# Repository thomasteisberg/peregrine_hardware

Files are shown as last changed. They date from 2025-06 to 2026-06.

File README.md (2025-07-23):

# Peregrine Hardware Files

This repository contains hardware design and fabrication files for the Peregrine UAV-borne radio echo sounder (Part of the ORCA project)

See https://orca.radioglaciology.com/docs/peregrine/ for details

Design files produced by us are available under an [MIT License](LICENSE). For vendor CAD, please check with individual vendors.

## Payload Enclosure

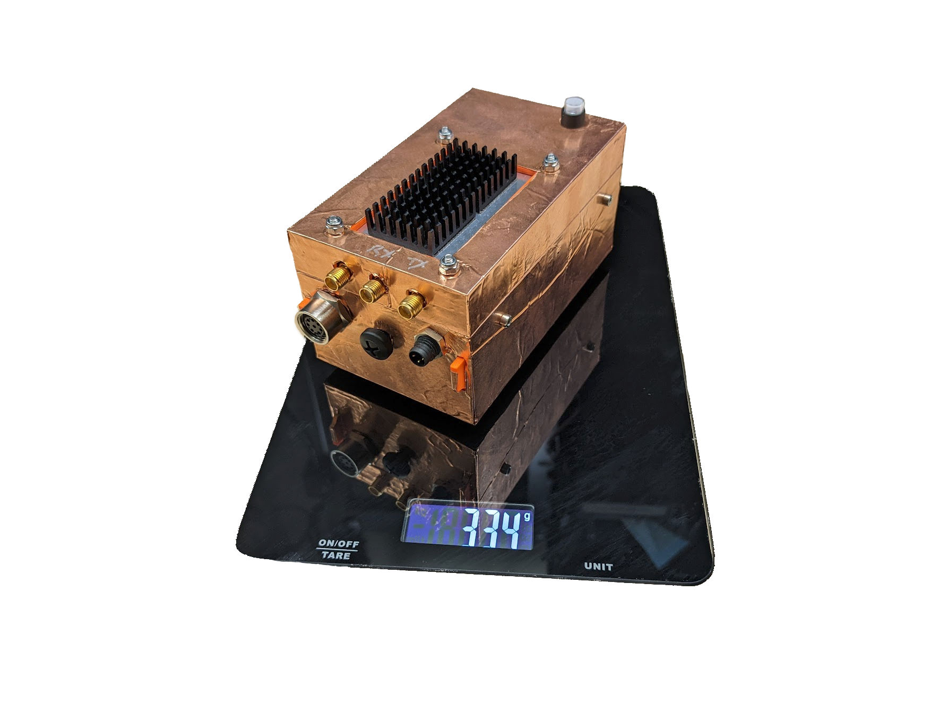
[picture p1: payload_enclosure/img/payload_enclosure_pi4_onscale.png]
Photo of an assembled payload enclosure


The [payload enclosure](payload_enclosure/) is the box containing the Ettus b205-mini SDR and the Raspberry Pi for the Peregrine UAS.

This assembly normally lives in the nosecone of the Peregrine UAV, as seen in the photo below, however it can be re-purpose in other ways.

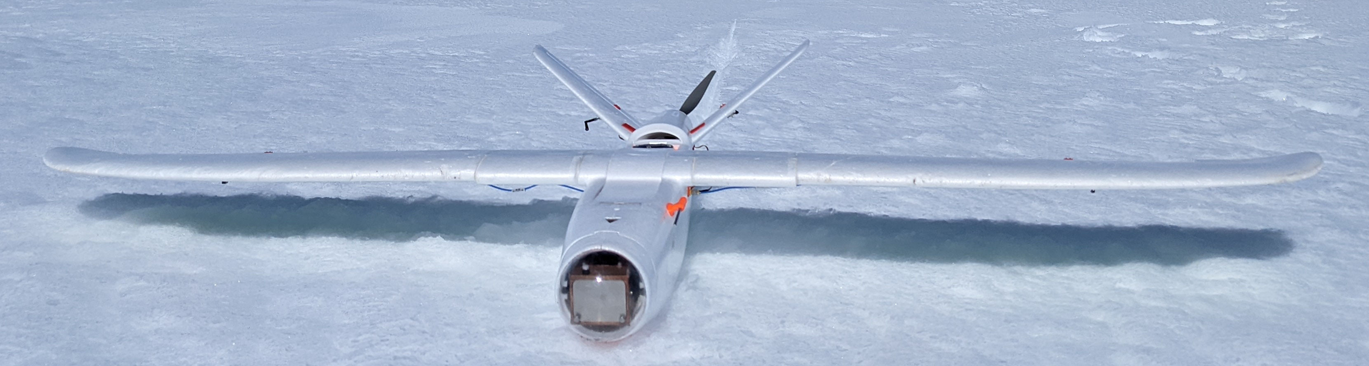
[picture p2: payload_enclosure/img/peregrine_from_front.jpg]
Front view of the Peregrine UAS showing the payload enclousure within the nosecone


## Payload enclosure PCBs

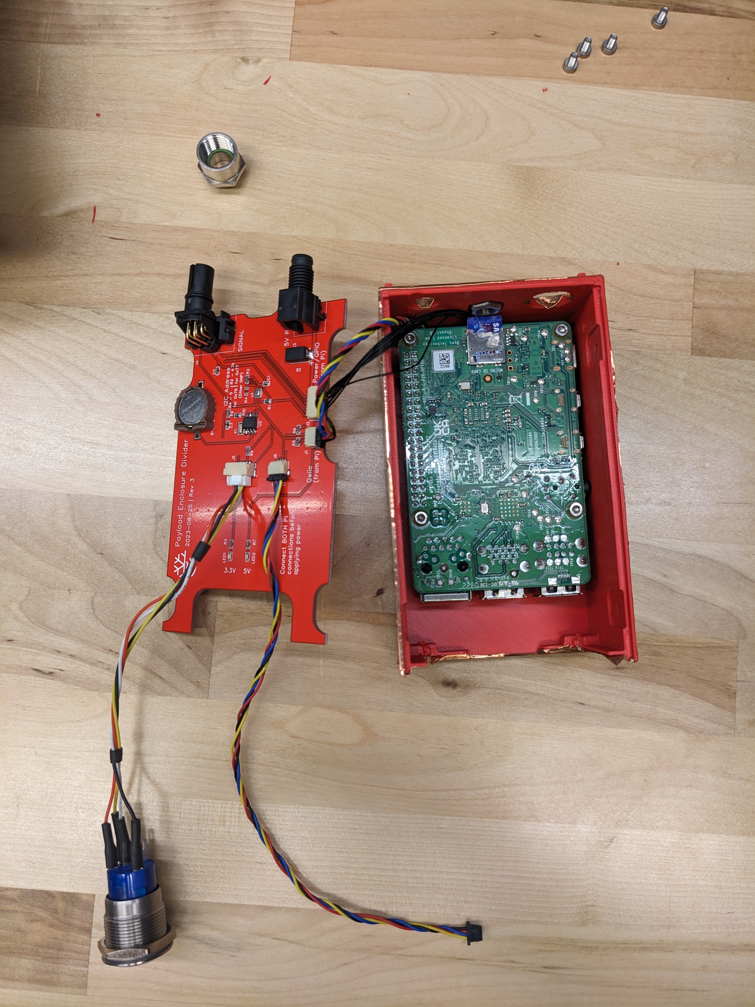
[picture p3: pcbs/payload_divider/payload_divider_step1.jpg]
Peregrine Payload Divider PCB


There are two custom PCBs that live inside the payload enclosure. They are:

* [Peregrine Pi Hat](pcbs/pi_hat/)
* [Peregrine Payload Divider](pcbs/payload_divider/)

## Other PCBs

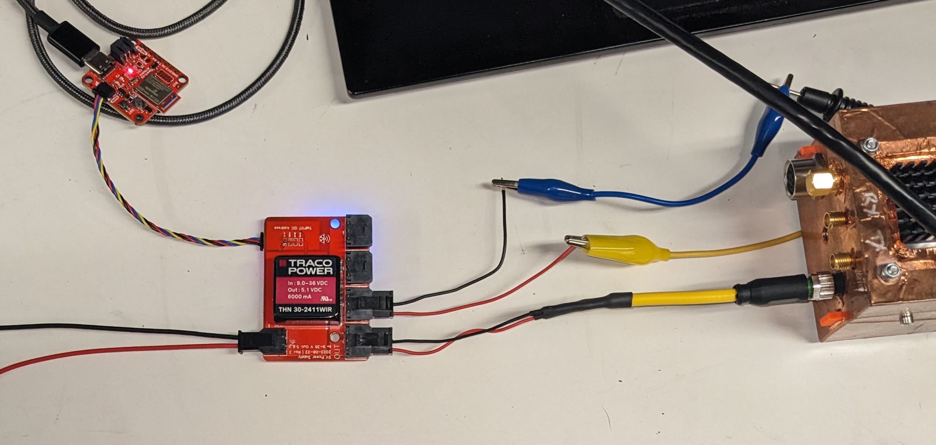
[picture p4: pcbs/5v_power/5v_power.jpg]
5V switching regulator PCBA


* [5V Switching Power Supply](pcbs/5v_power/)

## Antennas

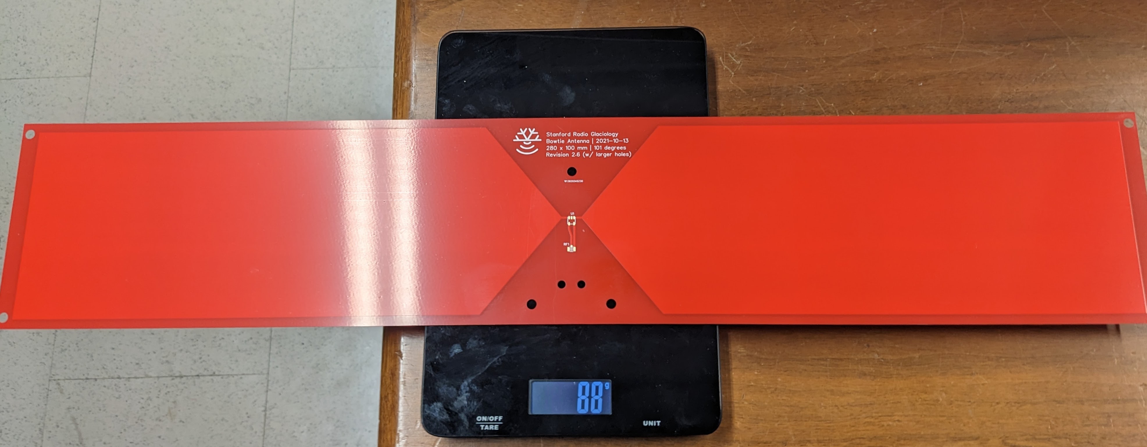
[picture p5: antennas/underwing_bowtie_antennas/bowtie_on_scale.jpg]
Bowtie antenna on a scale


* [Peregrine under-wing edge-cut bowtie antennas](antennas/underwing_bowtie_antennas/)

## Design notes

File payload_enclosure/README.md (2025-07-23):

# Peregrine Payload Enclosure

This is the main radar payload enclosure for Peregrine.

See https://orca.radioglaciology.com/docs/peregrine/payload/ for details.

The `design_files` directory has STEP assembly files and Autodesk Inventor
[Pack and Go files](https://help.autodesk.com/view/INVNTOR/2025/ENU/?guid=GUID-730304AA-13BD-467B-9351-C7C1362876BD)
fpr each of the variants described below.

The `fabrication_files_(variant)` contain ready-to-use files for fabrication. See [fabrication notes](#fabrication) below.

### Payload enclosure PCBs

There are also two custom PCBs that live inside the payload enclosure. They are:

* [Peregrine Pi Hat](../pcbs/pi_hat/)
* [Peregrine Payload Divider](../pcbs/payload_divider/)

## Variants

There are three variants included here:

### Pi 5

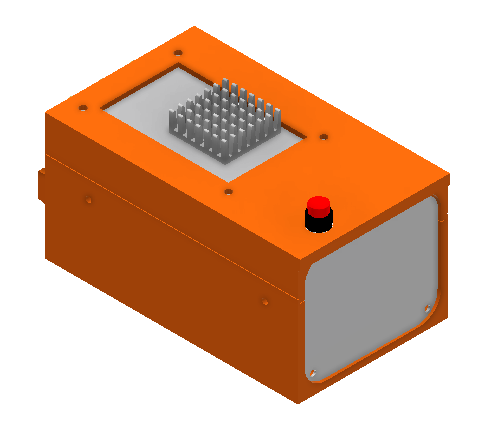
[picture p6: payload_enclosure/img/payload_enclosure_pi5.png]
Payload enclousure with Pi 5 CAD rendering


This version fits in the Peregrine nosecone and contains a Raspberry Pi 5.

This version is identical to the Pi 4 version except for an different heatsink design.

### Pi 5 with NVMe SSD

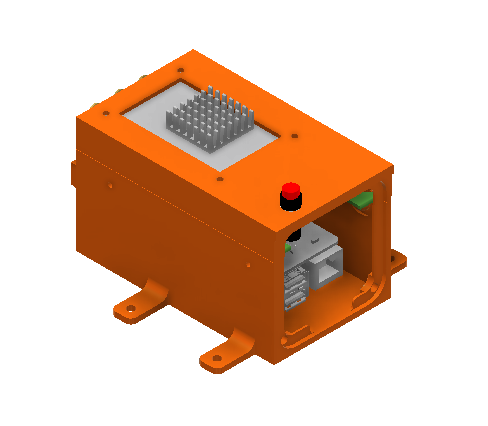
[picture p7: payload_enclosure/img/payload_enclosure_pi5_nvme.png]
Extended height payload enclosure with Pi 5 and an NVMe SSD


This is a variant of the above with the Pi-side of the shell vertically extended to make space for an NVMe SSD. See https://orca.radioglaciology.com/docs/peregrine/payload/data-storage/ for more information.

Note that because this is a vertically stretch version, it does not fit in the Peregrine nosecone without modification. This variant was designed for other uses and also has 4 mounting holes added on small tabs.

### Pi 4 (archived)

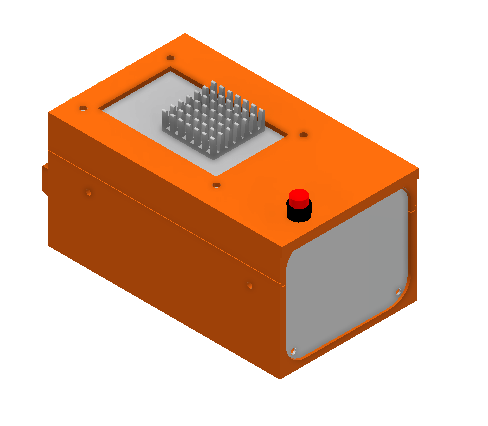
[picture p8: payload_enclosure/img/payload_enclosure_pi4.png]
Payload enclosure with Pi 4 CAD rendering


This version fits in the Peregrine nosecone and contains a Raspberry Pi 4.

For new builds, using the Raspberry Pi 5 is strongly recommended.

## Fabrication notes

### 3D Printing

The following components are intended to be 3D printed:

* `pi_shell.stl`
* `sdr_shell.stl`

They are designed for printing on an FDM printer. They should be printed in ASA
or a similar material (not PLA) to avoid warping due to the heat from the components
inside.

### Laser Cutting

The `cover_plate_2holes_standardfit_0p5mm_tolerance.dxf` file is intended for
laser cutting. Our default option is to cut this out of 1 mm (0.040") aluminum.
(We use SendCutSend's 5052 H32 Aluminum cutting service.)

For the Peregrine UAS, it can be useful to use this plate as a fine-tuning
adjustment for the center of gravity, since it sits in the very front of the
aircraft. For this purpose, our flight kit usually contains copies of this part
cut out of the following materials (all from SendCutSend):

* 1 mm 5052 Aluminum
* 1 mm Copper
* 1.5 mm Copper

This provides enough mass variation to be able to fine-tune the center of gravity
as needed.
(The adjustable battery tray provides the main center of gravity adjustment.
This is for minor fine-tuning only.)

### CNC Machining

The `pi(4/5)_heat_block.stp` and associated `pi(4/5)_heat_block.pdf` files are
intended for CNC machining. The PDF file is a drawing that specifies the thread
tapping needed for the mounting holes.

We get this fabricated out of aluminum. We have used several CNC vendors with
good results every time.

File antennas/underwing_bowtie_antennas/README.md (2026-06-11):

# Peregrine Underwing Edge-Cut Bowtie Antenna

Bowtie antenna on a scale

This is the design for the edge-cut bowtie radar antennas mounted under the Peregrine wings.

The `.zip` file is an export from EasyEDA. It can be uploaded to EasyEDA as a new project. It is also possible to load in KiCAD using the EasyEDA importer (File > Import Non-KiCad Project ... > EasyEDA (JLCEDA) Std Backup).

The source project in EasyEDA is titled `bowtie-v2.6-with-larger-holes`.

## Production notes

This antenna is designed to be printed on standard FR4. FR4 is generally not controlled for dielectric permittivity, so results may vary and each individual unit should be checked for S11 before use.

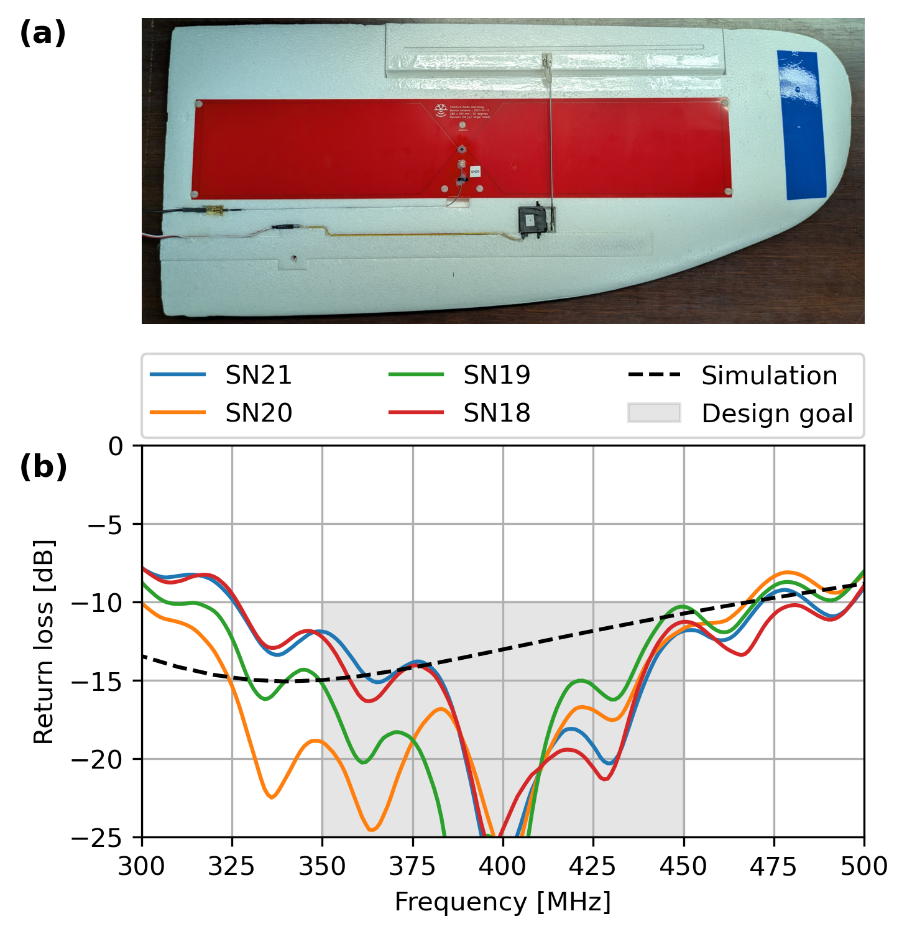
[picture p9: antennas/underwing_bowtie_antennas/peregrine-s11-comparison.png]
Antenna S11 results from several individual units


The design is not particularly sensitive to the FR4 thickness. For Peregrine, I had this produced on 0.6 mm FR4 substrate, which significantly reduces the weight. Note that 0.6mm FR4 substrate is not rigid on its own, which may be a downside depending on how you plan to use this.

The total width (588 mm) is larger than what many PCB manufacturers can do. We produced this PCB with PCBWay.

If you want to copy our settings exaclty, the design is shared on PCBWay: https://www.pcbway.com/project/shareproject/Peregrine_under_wing_bowtie_antenna_c198dc1e.html

## Bill of Materials

* U1 (balun): [Mini-Circuits TC4-1W+](https://www.minicircuits.com/WebStore/dashboard.html?model=TC4-1W%2B)
* RF1 (U.FL connector): [U.FL-R-SMT-1(40)](https://www.mouser.com/ProductDetail/Hirose-Connector/U.FL-R-SMT-140?qs=PABxe4V6HDrVNWAmh6WKgw%3D%3D&srsltid=AfmBOopH3k4K2ASrjq8ZP3SyGSTScw2wuCMmbPjLw4Hym1gIAsaXcrwh)
* Suggested U.FL to SMA cable: [CSI-SGFI-100-UFFR ](https://www.mouser.com/ProductDetail/TE-Connectivity-Linx-Technologies/CSI-SGFI-100-UFFR?qs=j%252B1pi9TdxUbVF8XdLr3HSg%3D%3D)
* Silicone adhesive: [EGS10C-20G](https://www.digikey.com/en/products/detail/chip-quik-inc/EGS10C-20G/10059587)

## Design notes

The design is loosely described in our first Peregrine paper: [Development of a UAV-Borne Pulsed Ice-Penetrating Radar System](https://doi.org/10.1109/IGARSS46834.2022.9883583) [[PDF]](https://www.thomasteisberg.com/assets/pdf/igarss2022_peregrine.pdf)

The design was inspried by this paper: [A 900MHz shielded bow-tie antenna system for ground penetrating radar](https://doi.org/10.1109/ICGPR.2010.5550125)

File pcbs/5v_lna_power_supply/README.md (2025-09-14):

# 5V LNA Power Supply

**This PCBA is NOT a core Peregrine component. It is part of the "Peregrine+" ground-based system. It may be useful for various customized setups. It should not be used for high current applications such as UAV motors.**

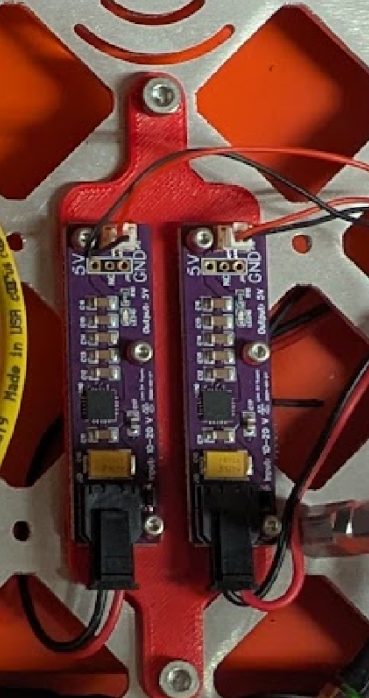
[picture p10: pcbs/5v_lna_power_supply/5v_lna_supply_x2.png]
Two 5V LNA power supplies in the SORA configuration


This project contains two simple designs for relatively low noise 5V power supplies intended to be used for powering low noise amplifiers. One is intended to be paired with a switching power supply providing slightly over 5V (such as the switching 5V supply in this repo configured to provide 5.2 or 5.3V). The other is a fully linear path from 10-20V input directly. The version we've used more extensively is the one that goes directly from the 10-20V version.

The `.zip` file is an export from EasyEDA. It can be uploaded to EasyEDA as a new project. It is also possible to load in KiCAD using the EasyEDA importer (File > Import Non-KiCad Project ... > EasyEDA (JLCEDA) Std Backup).

The source project in EasyEDA is titled `5v-lna-supply`.

## Fabrication notes

The Gerber files, BOM, and Pick and Place files are in the [fabrication_files](fabrication_files/) subdirectory. I've produced this PCB with JLCPCB in the past, but there's nothing particularly unique about the requirements. Any board house should be able to do it.

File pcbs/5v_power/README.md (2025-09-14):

# 5V Power for Peregine Payload

5V power PCB hooked up to a power supply, the radar payload, an a data logger

This is a simple PCB that hosts a high-quality switching 5V regulator from Traco: [THN 30-2411WIR](https://www.tracopower.com/model/thn-30-2411wir) (Note that this is a fairly expensive part -- about $80 in small quantity.)

This is used as the primary 5V power supply for the Peregrine UAV, powering both the radar and the rest of the UAV electronics. (It does not live inside the payload enclosure.)

There are detailed instructions for making the appropriate power harnessing on the main orca website: [5V Power Board and Power Harnesses](https://orca.radioglaciology.com/docs/peregrine/power/)

In addition to power regulation, the board has voltage, current, and temperature sensing, all available on an I2C bus with two [Qwiic](https://www.sparkfun.com/qwiic)-compatible connectors (for daisy-chaining). In the photo above, it is shown connected to a [SparkFun OpenLog Artemis](https://www.sparkfun.com/sparkfun-openlog-artemis.html) for bench logging of the sensor data. The I2C connection can also be connected to the data port on the radar payload and logged on the Pi using the [uav_radar_logger](https://github.com/thomasteisberg/uav_radar_logger) service.

The `.zip` file is an export from EasyEDA. It can be uploaded to EasyEDA as a new project. It is also possible to load in KiCAD using the EasyEDA importer (File > Import Non-KiCad Project ... > EasyEDA (JLCEDA) Std Backup).

The source project in EasyEDA is titled `uav-5v-supply-v4`.

**Note that this is NOT the version used on the Penguin UAV. That version has the same circuity but a different physical form factor.**

## Fabrication notes

The Gerber files, BOM, and Pick and Place files are in the [fabrication_files](fabrication_files/) subdirectory. I've produced this PCB with JLCPCB in the past, but there's nothing particularly unique about the requirements. Any board house should be able to do it.

For part availability and process reasons, I have never had any of the through-hole parts assembled by JLCPCB, however it should be fine to do so if your PCBA manufacturer has the parts in stock. The inductor (`L1`, TCK-141) is often not available in PCBA manufacturer part catalogs, so you may need to source and assemble that part separately.

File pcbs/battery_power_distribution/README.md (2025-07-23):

# Battery Power Distribution

**This PCBA is NOT a core Peregrine component. It is part of the "Peregrine+" ground-based system. It may be useful for various customized setups. It should not be used for high current applications such as UAV motors.**

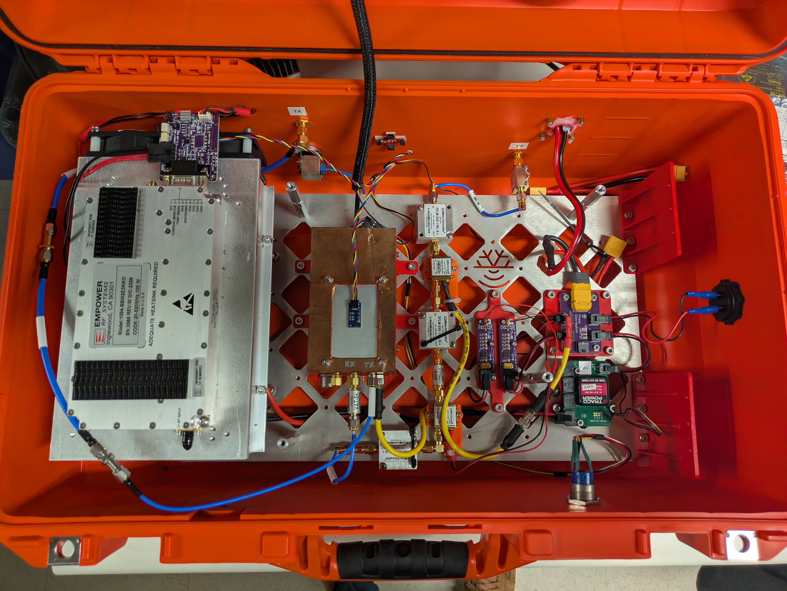
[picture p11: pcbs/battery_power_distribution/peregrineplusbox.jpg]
The Peregrine+ box, with the power distribution PCB visible on the right side


This is a very simple convenience PCB that connects an XT60 connector to 5 Molex Micro-Fit 3 2-pin connectors. It is used to cleanly wire up battery power to several components.

The `.zip` file is an export from EasyEDA. It can be uploaded to EasyEDA as a new project. It is also possible to load in KiCAD using the EasyEDA importer (File > Import Non-KiCad Project ... > EasyEDA (JLCEDA) Std Backup).

The source project in EasyEDA is titled `batt-power-distribution`.

## Fabrication notes

The Gerber files, BOM, and Pick and Place files are in the [fabrication_files](fabrication_files/) subdirectory. I've produced this PCB with JLCPCB in the past, but there's nothing particularly unique about the requirements. Any board house should be able to do it.

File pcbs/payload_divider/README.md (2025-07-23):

# Peregrine Payload Divider

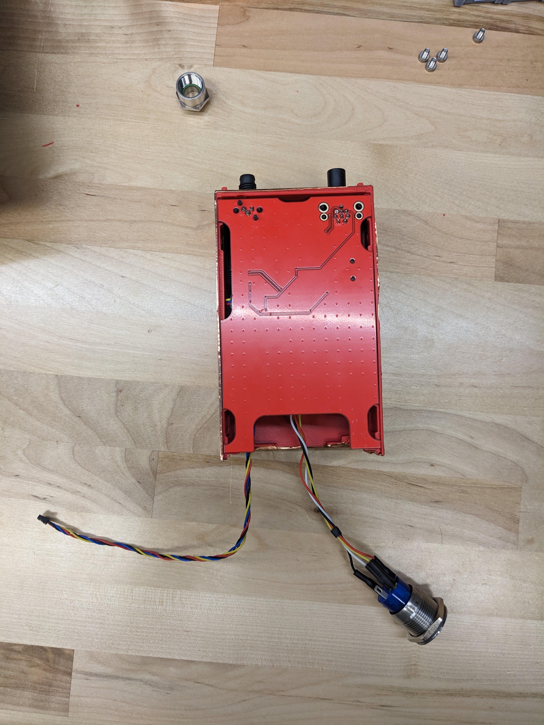
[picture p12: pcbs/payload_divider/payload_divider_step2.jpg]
Bottom side of the payload divider PCB after being placed in the payload enclosure
Payload divider PCB before being flipped into case 

The payload "divider" PCB divides the Raspberry Pi half of the shell from the SDR half of the shell. The PCB physically sits in the middle of the two clamshell pieces, hence its name.

This PCB serves as an external interface to the Pi as well as directly hosting a real-time clock and a temperature sensor. The external connectors to the payload enclosure live on this PCB.

The `.zip` file is an export from EasyEDA. It can be uploaded to EasyEDA as a new project. It is also possible to load in KiCAD using the EasyEDA importer (File > Import Non-KiCad Project ... > EasyEDA (JLCEDA) Std Backup).

The source project in EasyEDA is titled `payload-divider-v4`.

## Fabrication notes

The Gerber files, BOM, and Pick and Place files are in the [fabrication_files](fabrication_files/) subdirectory. I've produced this PCB with JLCPCB in the past, but there's nothing particularly unique about the requirements. Any board house should be able to do it.

For part availability and process reasons, I have never had any of the through-hole parts assembled by JLCPCB, however it should be fine to do so if your PCBA manufacturer has the parts in stock.

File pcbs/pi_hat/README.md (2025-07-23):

# Peregrine Pi Hat

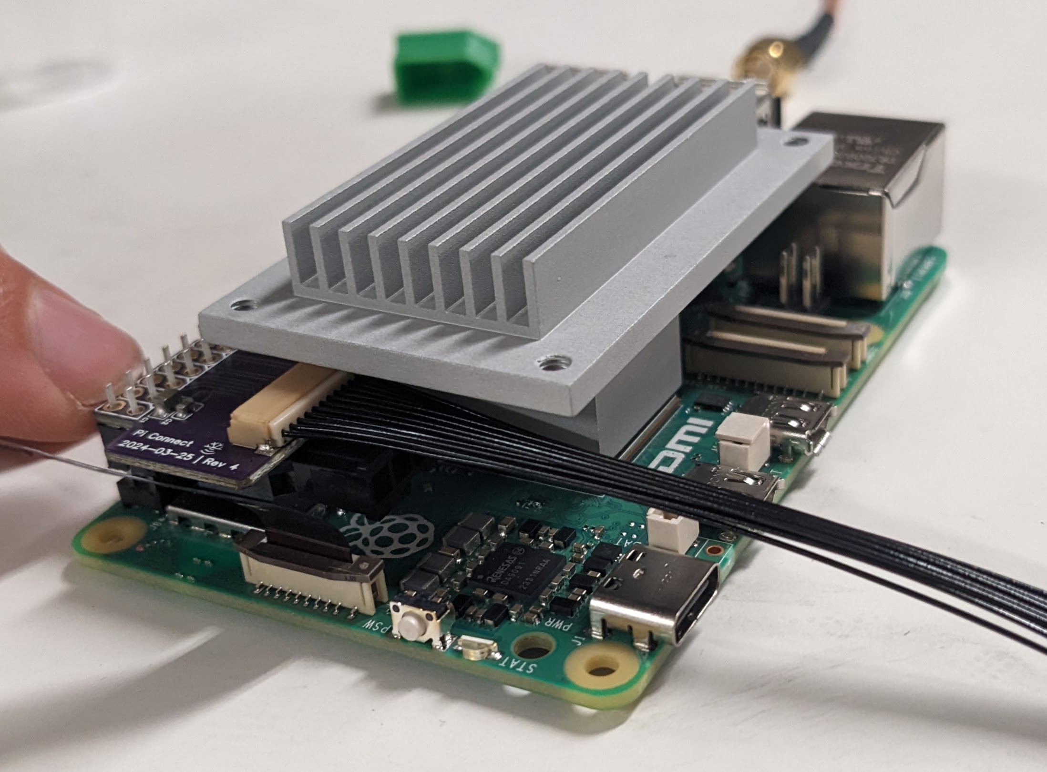
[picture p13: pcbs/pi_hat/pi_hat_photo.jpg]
Pi Hat installed on a Pi 5 under heatsink


This is a very small PCB whose only function is to interface with the power and I2C connections on the Pi's GPIO header. It's the purple board on the left of the photo above.

The `.zip` file is an export from EasyEDA. It can be uploaded to EasyEDA as a new project. It is also possible to load in KiCAD using the EasyEDA importer (File > Import Non-KiCad Project ... > EasyEDA (JLCEDA) Std Backup).

The source project in EasyEDA is titled `uav-pi-hat-v4`.

## Production notes

The Gerber files, BOM, and Pick and Place files are in the [fabrication_files](fabrication_files/) subdirectory. I've produced this PCB with JLCPCB in the past, but there's nothing particularly unique about the requirements. Any board house should be able to do it.

For part availability and process reasons, I have never had any of the through-hole parts assembled by JLCPCB. Read the next sentence to make sure you get the right female header!

**Important note:** The female header `J1` that connects to the Pi needs to be a low-profile header. The one in the schematic is just a placeholder. I believe that the one I've used is [CES-106-01-L-D](https://www.digikey.com/en/products/detail/samtec-inc/CES-106-01-L-D/6714165). If anyone wants to confirm this part works, I'd appreciate it.

## Design notes

The design is inspired by (but not really otherwise related to) SparkFun's [Qwiic SHIM](https://www.sparkfun.com/sparkfun-qwiic-shim-for-raspberry-pi.html).

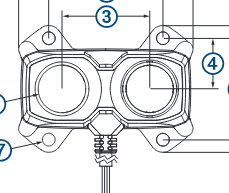
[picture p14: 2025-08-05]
mechanical/sensor_mounts/lidar_reference/lidar_lite_v3hp_top.png

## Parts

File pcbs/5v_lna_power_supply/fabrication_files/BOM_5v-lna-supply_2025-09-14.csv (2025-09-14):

ID | Name | Designator | Footprint | Quantity | Manufacturer Part | Manufacturer | Supplier | Supplier Part | Price
1 | BM02B-GHS-TBT (LF)(SN) | J12,J3 | CONN-SMD_2P-P1.25_BM02B-GHS-TBT-LF-SN | 2 | BM02B-GHS-TBT(LF)(SN) | JST | LCSC | C161690 | 0.1
2 | 22uF | C1 | C0805 | 1 | CC0805MKX5R7BB226 | YAGEO(国巨) | LCSC | C128856 | 0.06
3 | 10uF | C2 | C0603 | 1 | CC0603KRX5R5BB106 | YAGEO(国巨) | LCSC | C109455 | 0.012
4 | 1uF | C3,C4 | C0603 | 2 | CL10B105KO8NNNC | SAMSUNG | LCSC | C59782 | 0.005
5 | 47uF | C10 | CASE-D_7343 | 1 | TAJD476K025RNJ | Kyocera AVX | LCSC | C7228 | 0.576
6 | 10uF | C11,C12,C13,C14,C15,C16 | C1206 | 6 | C3216X5R1H106KT000N | TDK | LCSC | C329928 | 0.237
7 | 1uF | C17 | C0805 | 1 | C2012X7R1H105KT000N | TDK | LCSC | C76645 | 0.043
8 | MBR0530 | D10 | SOD-123_L2.8-W1.8-LS3.7-RD | 1 | MBR0530 | CJ(江苏长电/长晶) | LCSC | C77336 | 0.033
9 | 436500300 | J1 | CONN-TH_3P-436500300 | 1 | 436500300 | MOLEX | LCSC | C503478 | 0.347
10 | HDR-M-2.54_1x3 | J2,J11 | HDR-M-2.54_1X3 | 2 |  |  | LCSC | C180248 | 0.184
11 | 436500200 | J10 | CONN-TH_2P-P3.00_MOLEX_436500200 | 1 | 436500200 | MOLEX | LCSC | C192562 | 0.493
12 | LTST-C194TBKT | LED1,LED10 | LED0603-RD | 2 | LTST-C194TBKT | Lite-On | LCSC | C575417 | 0.067
13 | 1.5K | R1,R10 | R0603 | 2 | RC0603FR-071K5L | YAGEO | LCSC | C114668 | 0.001
14 | TPS7A2050PDBVR | U1 | SOT-23-5_L2.9-W1.6-P0.95-LS2.8-BR | 1 | TPS7A2050PDBVR | TI(德州仪器) | LCSC | C2864504 | 0.246
15 | TPS7A4700RGWR | U10 | VQFN-20_L5.0-W5.0-P0.65-TL-EP | 1 | TPS7A4700RGWR | TI(德州仪器) | LCSC | C114839 | 1.731

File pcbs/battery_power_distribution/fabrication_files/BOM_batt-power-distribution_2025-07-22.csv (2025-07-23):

ID | Name | Designator | Footprint | Quantity | Manufacturer Part | Manufacturer | Supplier | Supplier Part | Price
1 | 10uF | C1,C2 | C1206 | 2 | C3216X5R1H106KT000N | TDK | LCSC | C329928 | 0.245
2 | 4.7uF | C3 | C1812 | 1 | C4532X7S2A475KT000N | TDK | LCSC | C432933 | 0.968
3 | XT60PW-M | J1 | CONN-TH_XT60PW-M | 1 | XT60PW-M | AMASS(艾迈斯) | LCSC | C98732 | 0.581
4 | 436500200 | J2,J3,J4,J5,J6 | CONN-TH_2P-P3.00_MOLEX_436500200 | 5 | 436500200 | MOLEX | LCSC | C192562 | 0.514

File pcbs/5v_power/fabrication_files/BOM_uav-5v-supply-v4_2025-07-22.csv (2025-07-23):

ID | Name | Designator | Footprint | Quantity | Manufacturer Part | Manufacturer | Supplier | Supplier Part | Price
1 | 436500200 | CN1 | CONN-TH_2P-P3.00_MOLEX_436500200 | 1 | 436500200 | MOLEX | LCSC | C192562 | 0.514
2 | 436500300 | CN2,CN3,CN4,CN5 | CONN-TH_3P-436500300 | 4 | 436500300 | MOLEX | LCSC | C503478 | 0.342
3 | THN_30-2411WIR | PS1 | CONV_THN_30-2411WIR | 1
4 | 0 | 0X4A,0X4B,0X48,0X49 | R0603 | 4 | RMS06JT0 | TA-I Tech | LCSC | C209218 | 0.002
5 | SM04B-SRSS-TB (LF)(SN) | CN7,CN6 | CONN-SMD_4P-P1.00_SM04B-SRSS-TB-LF-SN | 2 | SM04B-SRSS-TB (LF)(SN) | JST Sales America | LCSC | C160404 | 0.192
6 | 100mΩ | R7 | R2512 | 1 | PT2512FK-7W0R1L | YAGEO(国巨) | LCSC | C309534 | 0.146
7 | 0Ω | R8 | R0603 | 1 | SFR03EZPJ000 | ROHM(罗姆) | LCSC | C510292 | 0.009
8 | INA219AIDR | U2 | SOIC-8_L4.9-W3.9-P1.27-LS6.0-BL | 1 | INA219AIDR | TI(德州仪器) | LCSC | C138706 | 0.721
9 | TCK-141-FIXED-FOOTPRINT | L1 | IND-SMD_L4.0-W4.0-LS4.7_TCK-141 COPY | 1 | TCK-141 | null | LCSC | C5160328 | 6.021
10 | 4.7uF | C1,C2,C3 | C1812 | 3 | C4532X7S2A475KT000N | TDK | LCSC | C432933 | 0.968
11 | 1nF | C4,C5 | C1808 | 2 | C4520X7R3D102KT000S | TDK | LCSC | C165828 | 0.851
12 | 100nF | C6 | C0603 | 1 | CC0603KRX7R9BB104 | YAGEO | LCSC | C14663 | 0.002
13 | LTST-C194TBKT | LED1 | LED0603-RD | 1 | LTST-C194TBKT | Lite-On | LCSC | C575417 | 0.055
14 | 19-213/R6C-AQ1R2B/3T | LED2 | LED0603-RD_RED | 1 | 19-213/R6C-AQ1R2B/3T | Everlight Elec | LCSC | C128249 | 0.039
15 | 1.5K | R1 | R0603 | 1 | RC0603FR-071K5L | YAGEO | LCSC | C114668 | 0.001
16 | 39kΩ | R2 | R0603 | 1 | RT0603FRE0739KL | YAGEO(国巨) | LCSC | C706166 | 0.01
17 | 10.7K | R3 | R0603 | 1 | 0603WAF1072T5E | UniOhm | LCSC | C22857 | 0.001
18 | 2.2K | R4,R5 | R0603 | 2 | 0603WAF2201T5E | UniOhm | LCSC | C4190 | 0.001
19 | 1K | R6 | R0603 | 1 | AF0603FR-071KL | YAGEO | LCSC | C144087 | 0.004
20 | TMP117AIDRVR | U1 | WDFN-6_L2.0-W2.0-P0.65-TL-EP | 1 | TMP117AIDRVR | TI(德州仪器) | LCSC | C699536 | 1.322

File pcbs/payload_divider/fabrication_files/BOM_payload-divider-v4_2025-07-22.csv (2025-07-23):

ID | Name | Designator | Footprint | Quantity | Manufacturer Part | Manufacturer | Supplier | Supplier Part | Price
1 | 436500300 | J7 | CONN-TH_3P-436500300 | 1 | 436500300 | MOLEX | LCSC | C503478 | 0.342
2 | 1uF | C4,C5 | C0603 | 2 | CL10B105KO8NNNC | SAMSUNG | LCSC | C59782 | 0.005
3 | SM12B-SRSS-TB(LF)(SN) | J2 | CONN-TH_SM12B-SRSS-TB-LF-SN | 1 | SM12B-SRSS-TB(LF)(SN) | JST | LCSC | C160411 | 0.359
4 | AP7365-33WG-7 | U3 | SOT-25_L3.0-W1.6-P0.95-LS2.8-BR | 1 | AP7365-33WG-7 | DIODES | LCSC | C150742 | 0.157
5 | CR1220-2 | B1 | BAT-SMD_CR1220-2 | 1 | CR1220-2 | Q&J | LCSC | C70381 | 0.236
6 | 10uF | C3 | C0603 | 1 | CC0603KRX5R5BB106 | YAGEO(国巨) | LCSC | C109455 | 0.013
7 | 1kΩ | R9 | R0603 | 1 | AF0603FR-071KL | YAGEO(国巨) | LCSC | C144087 | 0.004
8 | 0Ω | R10 | R0603 | 1 | RC0603FR-070RL | YAGEO(国巨) | LCSC | C100044 | 0.001
9 | PCF8523T/1,118 | U2 | SOP-8_L4.9-W3.9-P1.27-LS6.0-BL | 1 | PCF8523T/1,118 | NXP(恩智浦) | LCSC | C2651516 | 1.076
10 | - | X1 | OSC-SMD_L3.2-W1.5 | 1 | SC-32S32.768kHz20PPM12.5pF | Seiko(精工) | LCSC | C97606 | 0.183
11 | ECASD61C107M012KA0 | C6 | C2917 | 1 | ECASD61C107M012KA0 | Murata | Digi-Key | 490-ECASD61C107M012KA0CT-ND
12 | 150Ω | R8 | R0603 | 1 | 0603WAF1500T5E | UNI-ROYAL(厚声) | LCSC | C22808 | 0.001
13 | SM04B-SRSS-TB (LF)(SN) | J6 | CONN-SMD_4P-P1.00_SM04B-SRSS-TB-LF-SN | 1 | SM04B-SRSS-TB (LF)(SN) | JST Sales America | LCSC | C160404 | 0.192
14 | 100nF | C1,C2 | C0603 | 2 | CC0603KRX7R9BB104 | YAGEO | LCSC | C14663 | 0.002
15 | 2-2172067-2 | J3 | 221720672 | 1
16 | 43-02639 | J4 | 4302639 | 1
17 | 4.7K | R1,R2,R5,R6 | R0603 | 4 | RC0603FR-074K7L | YAGEO | LCSC | C99782 | 0.001
18 | 1K | R3 | R0603 | 1 | AF0603FR-071KL | YAGEO | LCSC | C144087 | 0.004
19 | 0 | R4 | R0603 | 1 | RC0603FR-070RL | YAGEO | LCSC | C100044 | 0.001
20 | BME280 | U1 | LGA-8_BME280_BL | 1 | BME280 | Bosch | LCSC | C92489 | 3.099
21 | SM05B-GHS-TB(LF)(SN) | J5 | CONN-SMD_5P-P1.25_SM05B-GHS-TB-LF-SN | 1 | SM05B-GHS-TB(LF)(SN) | JST Sales America | LCSC | C189896 | 0.174
22 | LTST-C190KRKT | LED1 | LED0603-RD_RED | 1 | LTST-C190KRKT | LITEON | LCSC | C94869 | 0.018
23 | LTST-C194TBKT | LED2 | LED0603-RD | 1 | LTST-C194TBKT | Lite-On | LCSC | C575417 | 0.055
24 | 1.5K | R7 | R0603 | 1 | RC0603FR-071K5L | YAGEO | LCSC | C114668 | 0.001

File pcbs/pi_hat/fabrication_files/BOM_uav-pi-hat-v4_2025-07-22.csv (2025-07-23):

ID | Name | Designator | Footprint | Quantity | Manufacturer Part | Manufacturer | Supplier | Supplier Part | Price
1 | SM12B-SRSS-TB(LF)(SN) | J2 | CONN-TH_SM12B-SRSS-TB-LF-SN | 1 | SM12B-SRSS-TB(LF)(SN) | JST | LCSC | C160411 | 0.359
2 | 436500312 | J3 | CONN-SMD_436500312 | 1 | 436500312 | MOLEX | LCSC | C114109 | 1.012
3 | 22uF | C1 | C0805 | 1 | CC0805MKX5R7BB226 | YAGEO(国巨) | LCSC | C128856 | 0.056
4 | 10uF | C2 | C0603 | 1 | CC0603KRX5R5BB106 | YAGEO(国巨) | LCSC | C109455 | 0.013
5 | 2.54-2X6PIN-1T | J1 | HDR-TH_12P-P2.54-V-M-R2-C6-S2.54_MOLEX_PIN1-NC | 1 | 2.54-2X6PIN-1T | null | LCSC | C9900005141

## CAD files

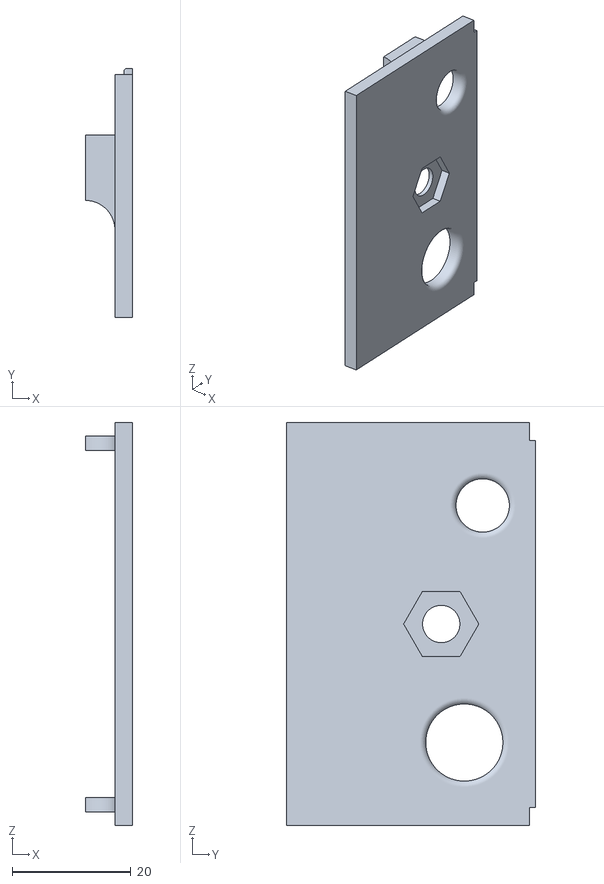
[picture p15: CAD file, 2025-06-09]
payload_enclosure/assembly_tooling/pi_shell_drill_guide_full.stl
8.00 x 42.0 x 68.0

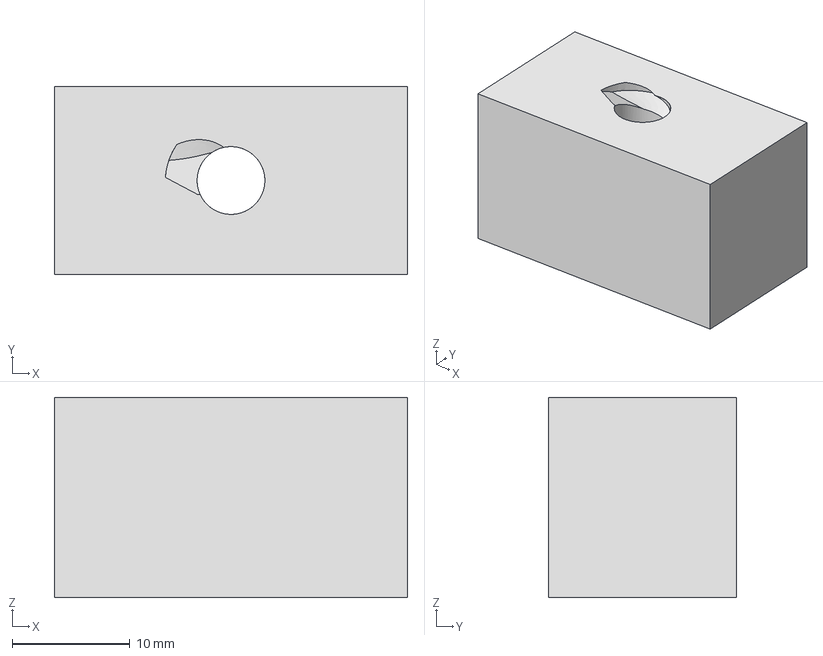
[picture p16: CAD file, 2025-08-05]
mechanical/antenna_anchors/block.stp
30.0 x 16.0 x 17.0 mm

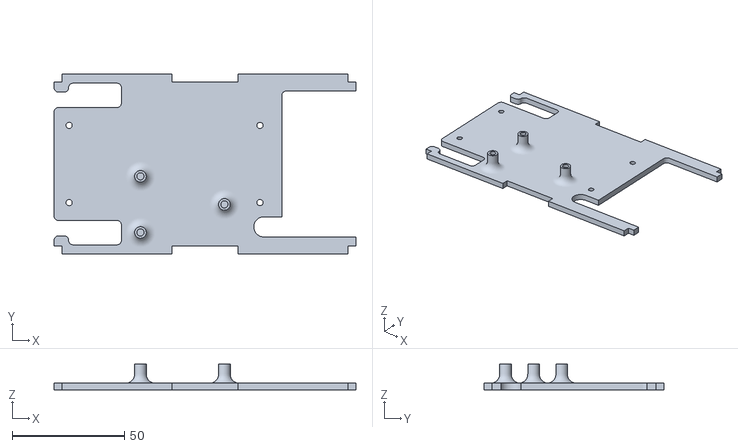
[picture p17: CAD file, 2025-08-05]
mechanical/avionics_mount/base.stl
134.5 x 80.0 x 11.5

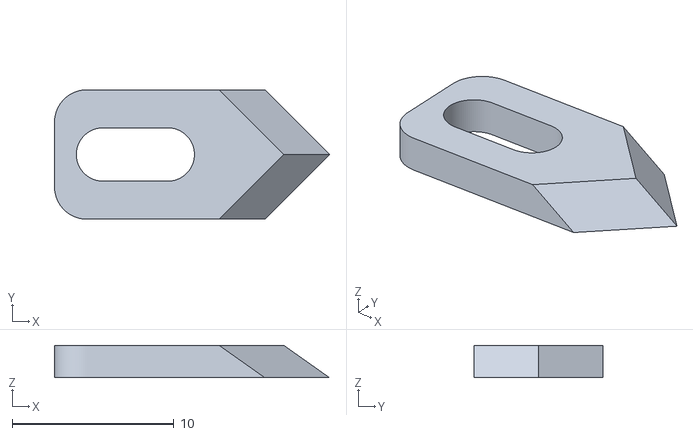
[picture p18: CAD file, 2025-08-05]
mechanical/back_lid_mount/back_lid_mount.stl
17.0 x 8.00 x 2.00

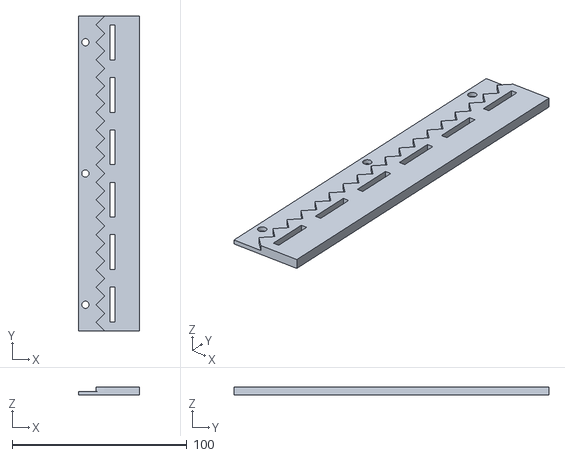
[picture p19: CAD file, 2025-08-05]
mechanical/battery_tray/tray_side_top.stl
35.0 x 180.0 x 4.50

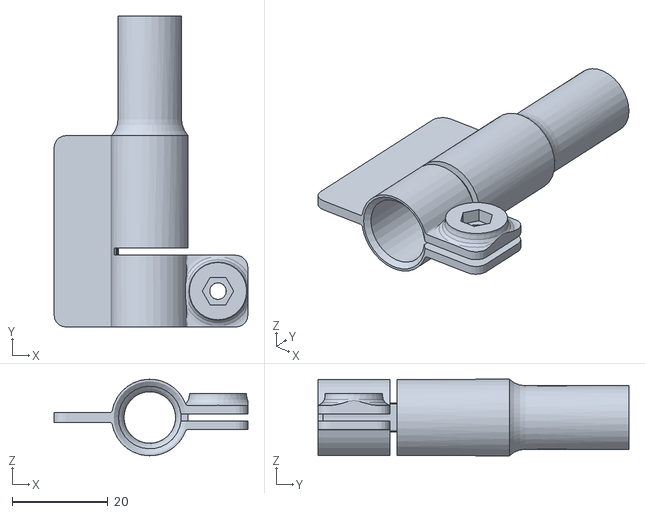
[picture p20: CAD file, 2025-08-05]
mechanical/custom_wing_spars/tube_clamp_l.stl
40.5 x 65.0 x 16.0

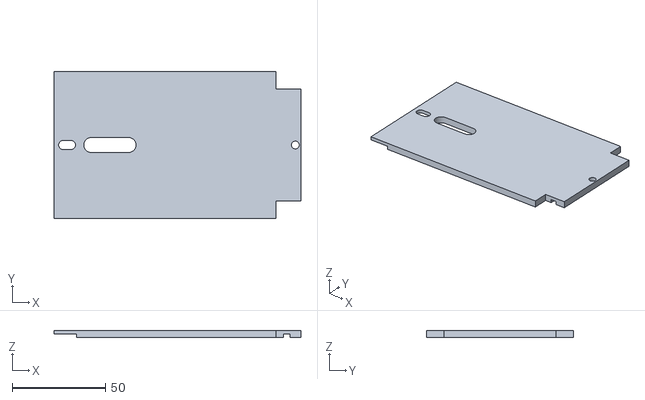
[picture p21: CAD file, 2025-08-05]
mechanical/sensor_mounts/gps_cover_flat_only.stl
132.5 x 79.0 x 4.00

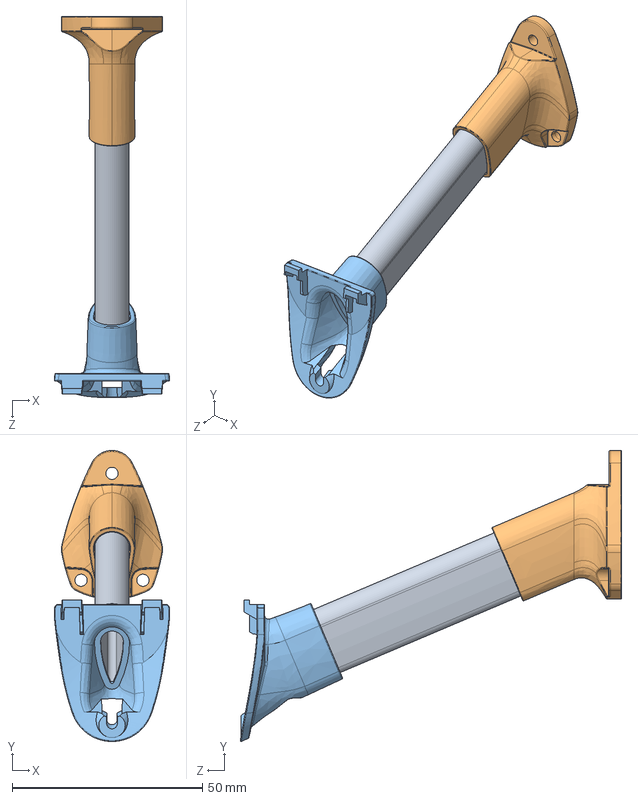
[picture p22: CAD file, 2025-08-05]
mechanical/sensor_mounts/here3_mount_reference/Here3_Istand.STEP
30.3 x 76.5 x 100.2 mm
77mm.STEP
btm_stand_base_20201107.STEP
gps_here3_holder_hex_20200919.STEP

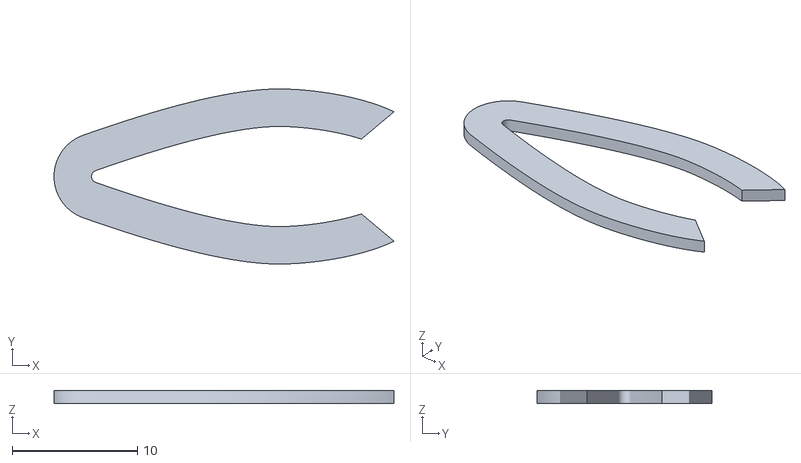
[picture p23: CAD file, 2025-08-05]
mechanical/sensor_mounts/pitot_custom/pitot_clip.stl
27.2 x 14.0 x 1.00

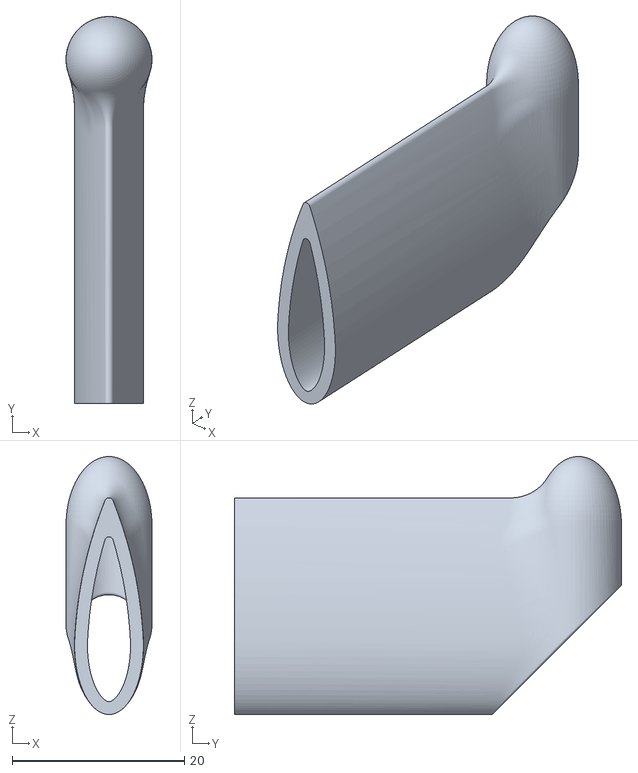
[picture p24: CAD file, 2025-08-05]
mechanical/sensor_mounts/pitot_from_internet/pitot_holder_1.STL
10.00 x 45.0 x 30.0

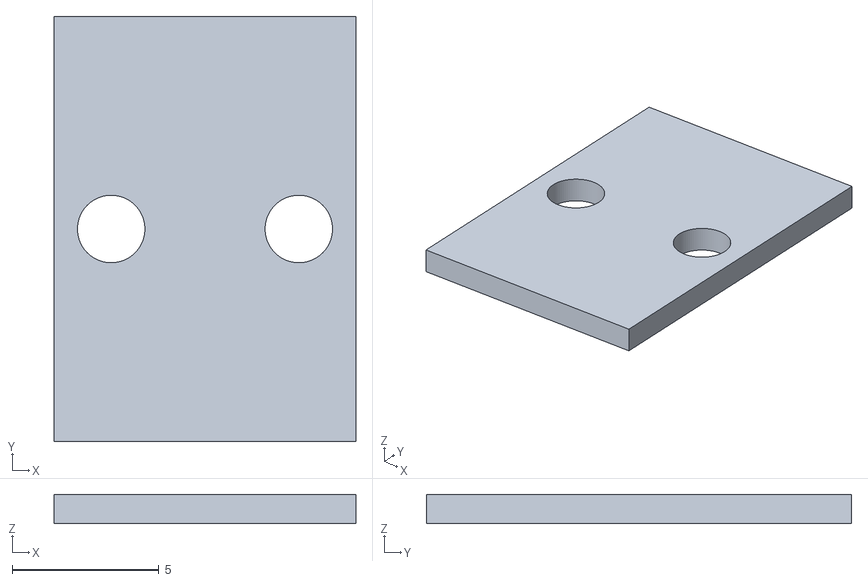
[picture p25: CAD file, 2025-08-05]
mechanical/servo_mounting/control_arm_backplate_mount.stl
10.3 x 14.5 x 1.00

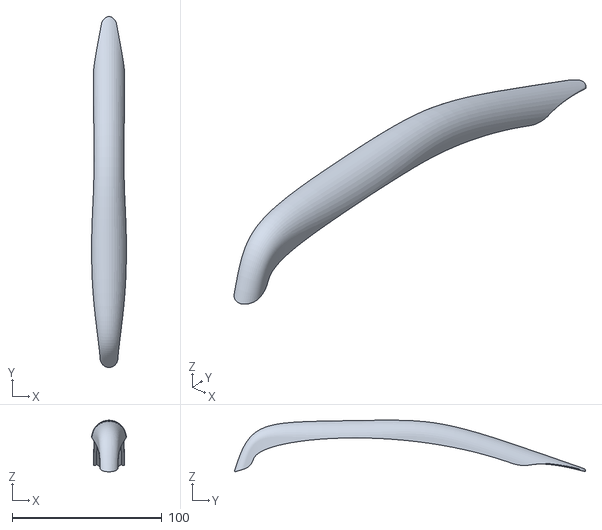
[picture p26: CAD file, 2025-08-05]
mechanical/skids/Talon_Skid_Print.STL
23.2 x 234.3 x 34.5

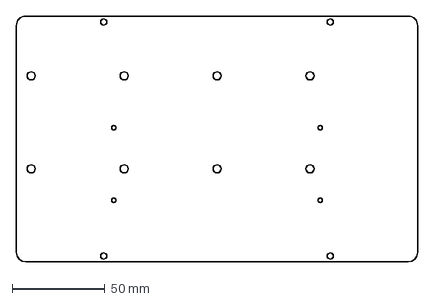
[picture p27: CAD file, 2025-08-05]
other_projects/sora/amplifier_tray.dxf
215.9 x 132.1 mm

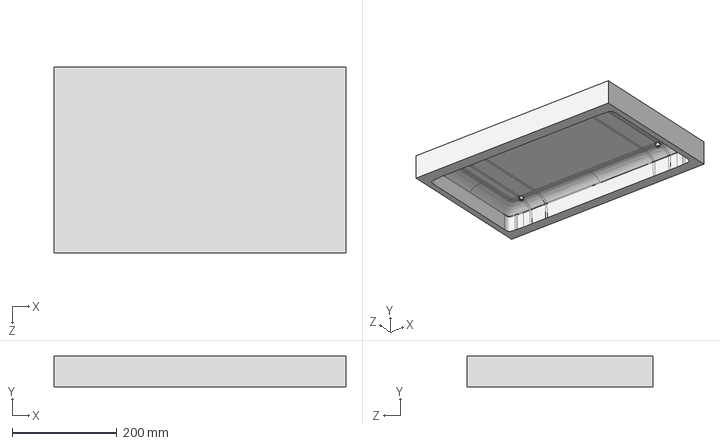
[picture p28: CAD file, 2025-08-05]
other_projects/sora/reference_cad/1535_step/1535 Top Tub.STEP
557.8 x 58.8 x 354.8 mm

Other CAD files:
mechanical/vtail_mounting/vtail_cutout_sketch.dwg
payload_enclosure/assembly_tooling/pi_shell_drill_guide_pilot.stl
payload_enclosure/fabrication_files_pi4/pi_shell.stl
payload_enclosure/fabrication_files_pi5/sdr_shell.stl
mechanical/antenna_anchors/66615A7_Female Drilling Anchors.STEP
mechanical/antenna_anchors/66615A7_Female Drilling Anchors_thickened.ipt
mechanical/antenna_anchors/66615A7_Female Drilling Anchors_thickened.stp
mechanical/antenna_anchors/OldVersions/66615A7_Female Drilling Anchors_thickened.0001.ipt
mechanical/antenna_anchors/OldVersions/block.0006.ipt
mechanical/antenna_anchors/block.ipt
mechanical/antenna_anchors/block.stl
mechanical/antenna_anchors/tapping_helper.ipt
mechanical/antenna_anchors/tapping_helper.stl
mechanical/avionics_mount/OldVersions/base.0006.ipt
mechanical/avionics_mount/OldVersions/base_herelink.0001.ipt
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

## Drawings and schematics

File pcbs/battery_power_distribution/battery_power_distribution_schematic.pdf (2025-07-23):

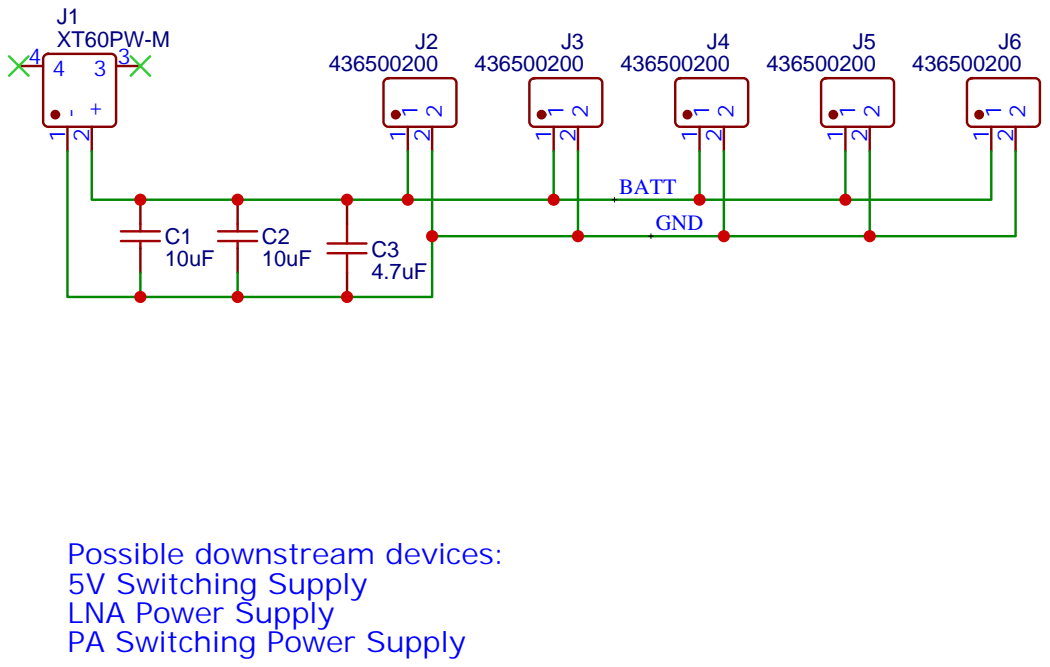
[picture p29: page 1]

Possible downstream devices:
5V Switching Supply
LNA Power Supply
PA Switching Power Supply

Company: Stanford Radio Glaciology

Drawn By: Thomas Teisberg

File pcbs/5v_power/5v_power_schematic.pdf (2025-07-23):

# 5V Power LED Indicator

# 5V, 30 W DC-DC Converter

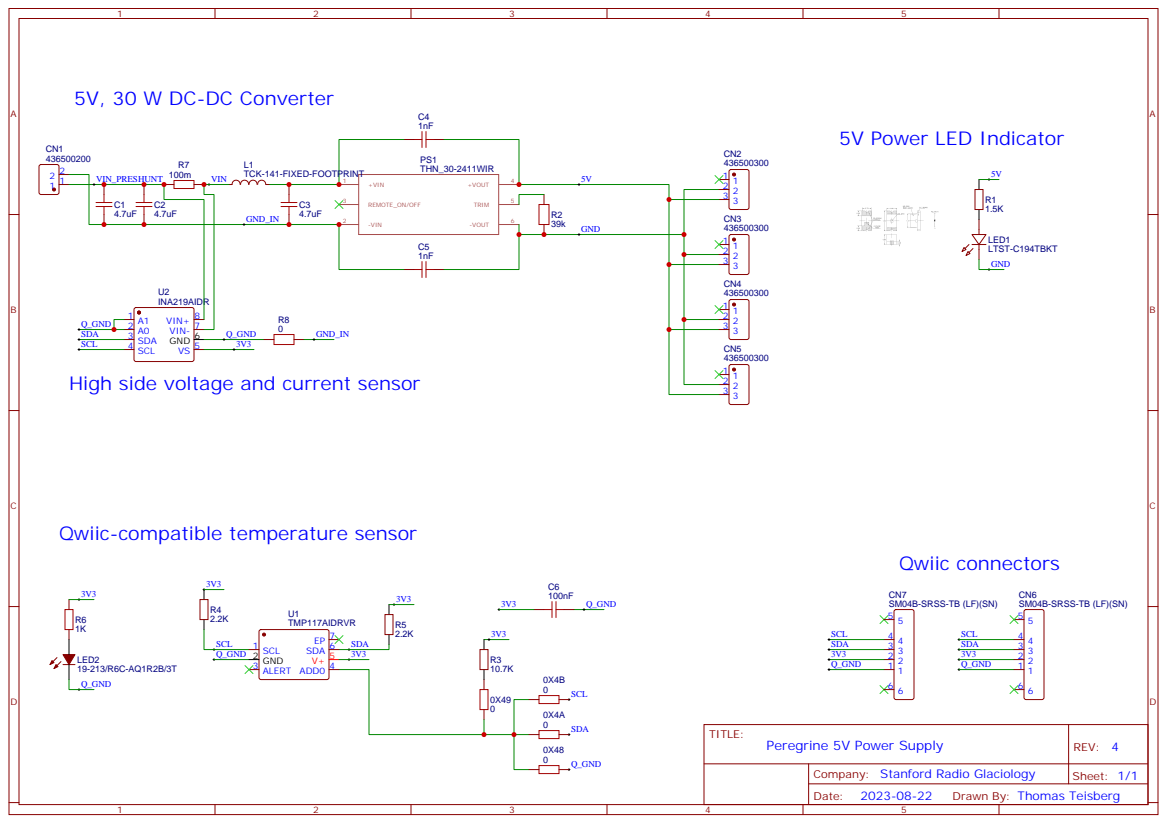
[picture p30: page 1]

Qwiic-compatible temperature sensor

Company: Stanford Radio Glaciology

Drawn By: Thomas Teisberg

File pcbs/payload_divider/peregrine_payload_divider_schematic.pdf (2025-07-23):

A | A

1

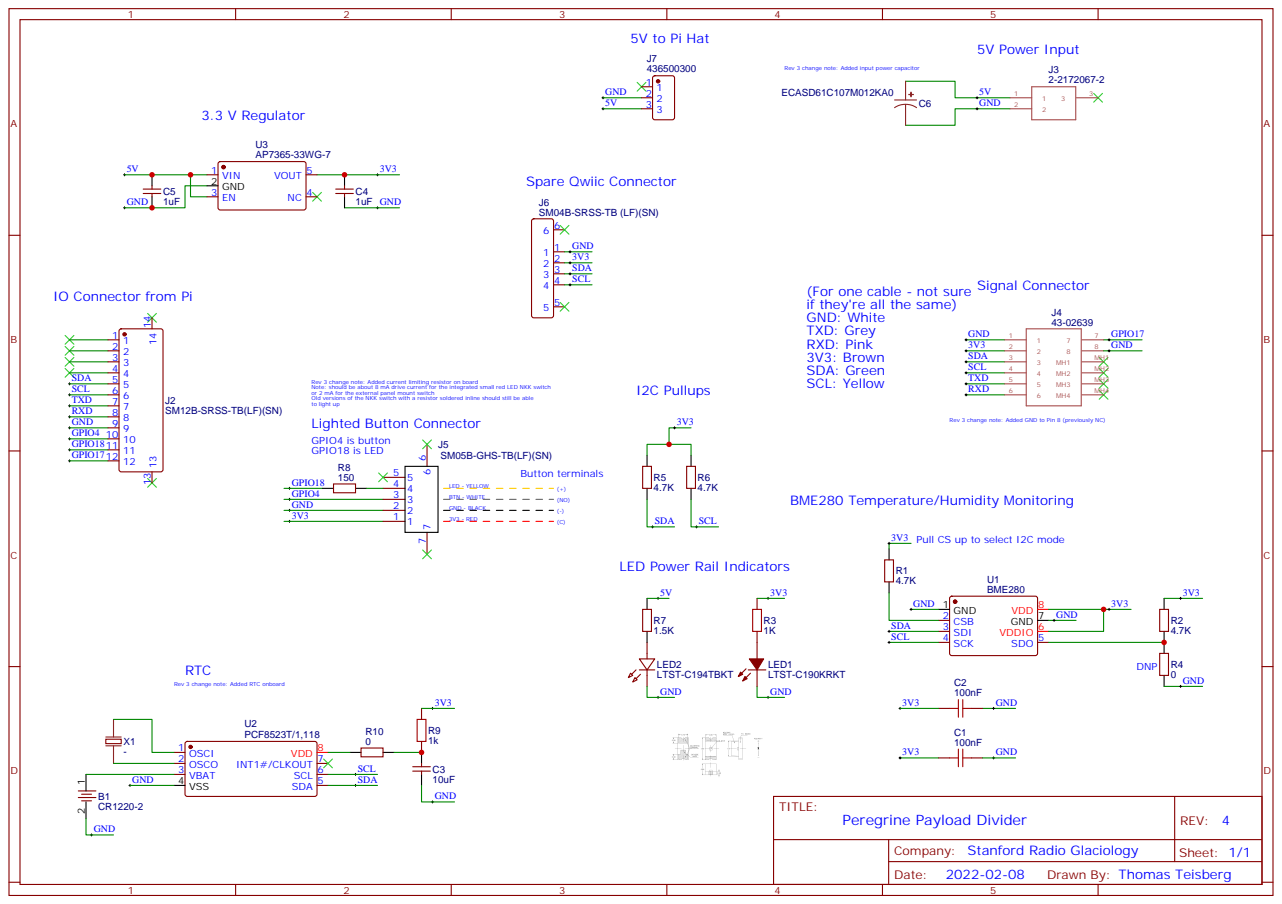
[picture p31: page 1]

Rev 3 change note: Added input power capacitor
ECASD61C107M012KA0

IO Connector from Pi

(For one cable - not sure
if they're all the same)
GND: White
TXD: Grey
RXD: Pink
3V3: Brown
SDA: Green
SCL: Yellow

Rev 3 change note: Added current limiting resistor on board
Note: should be about 8 mA drive current for the integrated small red LED NKK switch
or 2 mA for the external panel mount switch
Old versions of the NKK switch with a resistor soldered inline should still be able
to light up
Lighted Button Connector
GPIO4 is button
GPIO18 is LED

SM12B-SRSS-TB(LF)(SN)

Rev 3 change note: Added GND to Pin 8 (previously NC)

3V3 Pull CS up to select I2C mode

LED Power Rail Indicators

Rev 3 change note: Added RTC onboard

Company: Stanford Radio Glaciology

Drawn By: Thomas Teisberg

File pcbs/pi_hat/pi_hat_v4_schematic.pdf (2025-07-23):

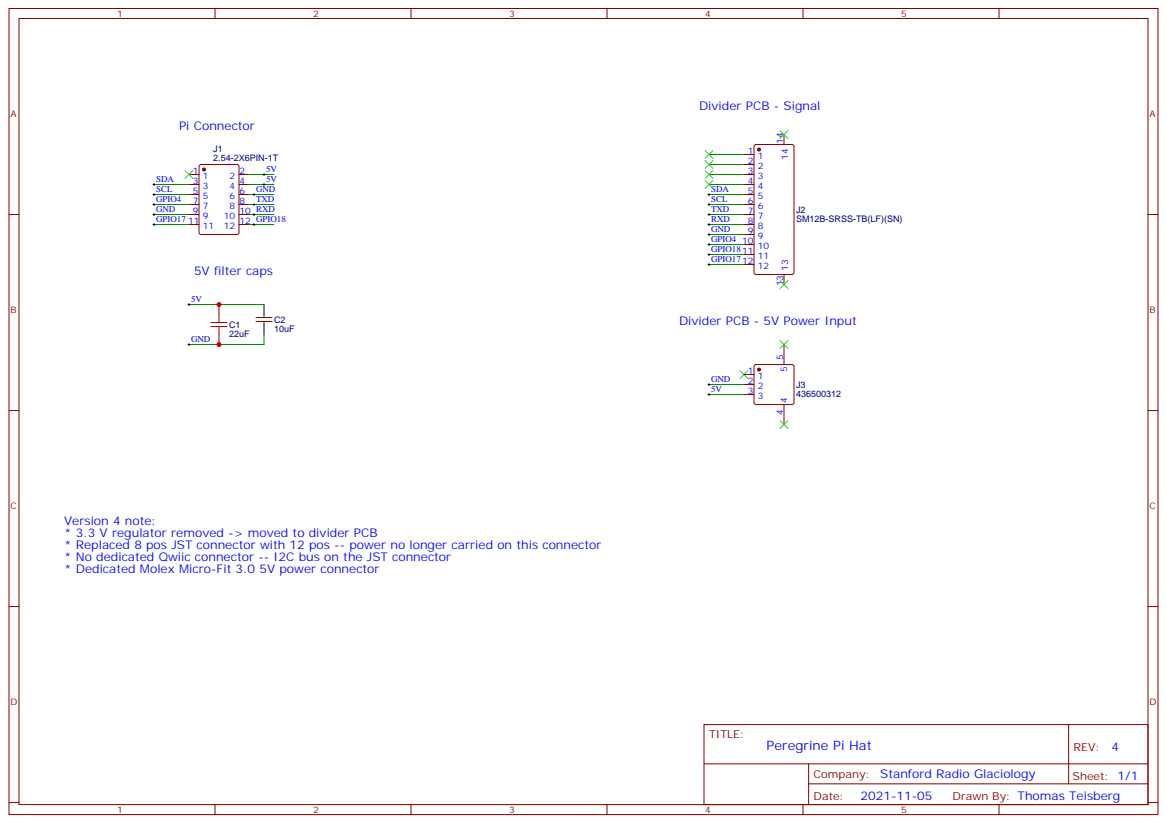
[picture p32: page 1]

SM12B-SRSS-TB(LF)(SN)

Divider PCB - 5V Power Input

Version 4 note:
* 3.3 V regulator removed -> moved to divider PCB
* Replaced 8 pos JST connector with 12 pos -- power no longer carried on this connector
* No dedicated Qwiic connector -- I2C bus on the JST connector
* Dedicated Molex Micro-Fit 3.0 5V power connector

Company: Stanford Radio Glaciology

Drawn By: Thomas Teisberg

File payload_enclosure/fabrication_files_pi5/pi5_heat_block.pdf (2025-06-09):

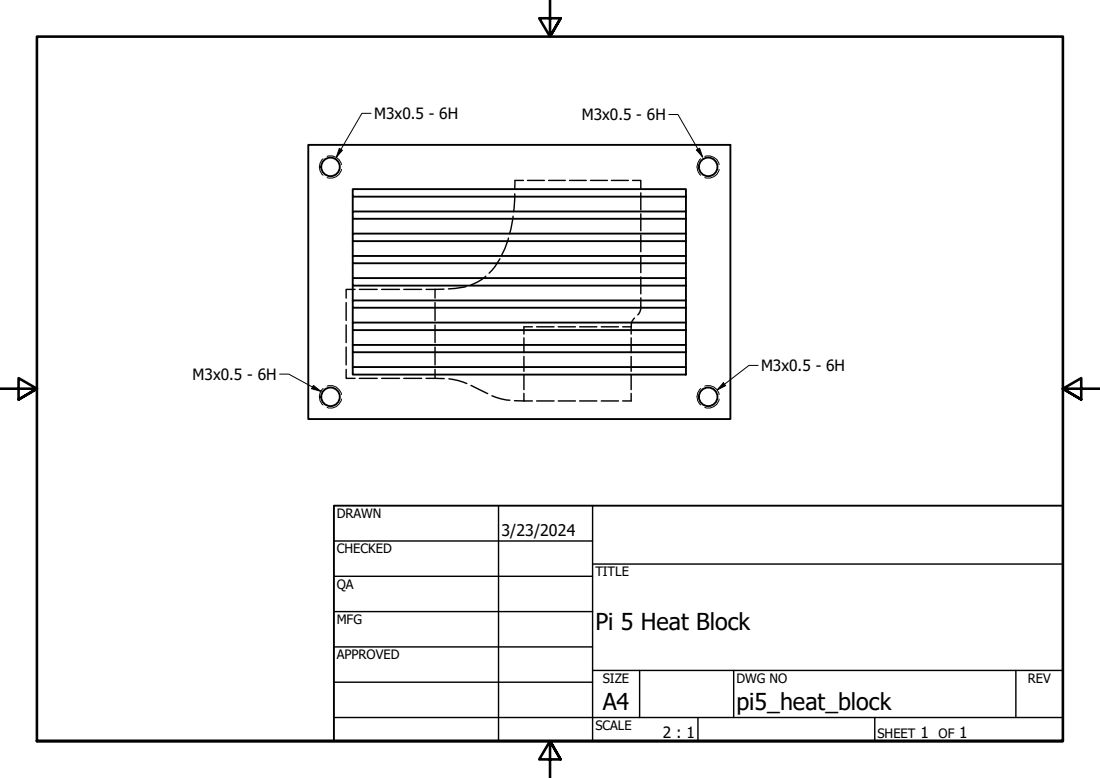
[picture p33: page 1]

DRAWN | 3/23/2024

CHECKED

Pi 5 Heat Block

MFG

APPROVED

SIZE A4 | DWG NO pi5_heat_block | REV

SCALE 2 : 1 | | SHEET 1 OF 1

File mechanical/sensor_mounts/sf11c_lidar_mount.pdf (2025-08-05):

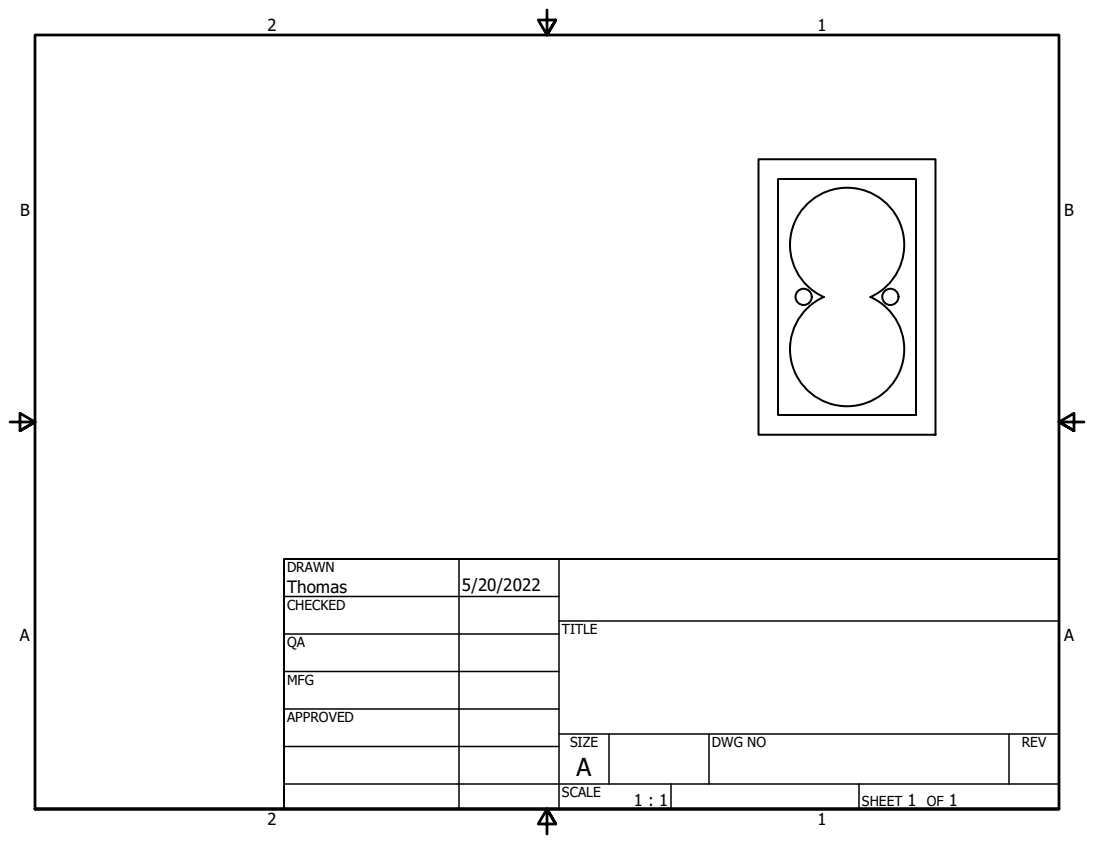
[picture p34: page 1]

DRAWN Thomas | 5/20/2022

CHECKED

MFG

APPROVED

SIZE A | DWG NO | REV

SCALE 1 : 1 | | SHEET 1 OF 1

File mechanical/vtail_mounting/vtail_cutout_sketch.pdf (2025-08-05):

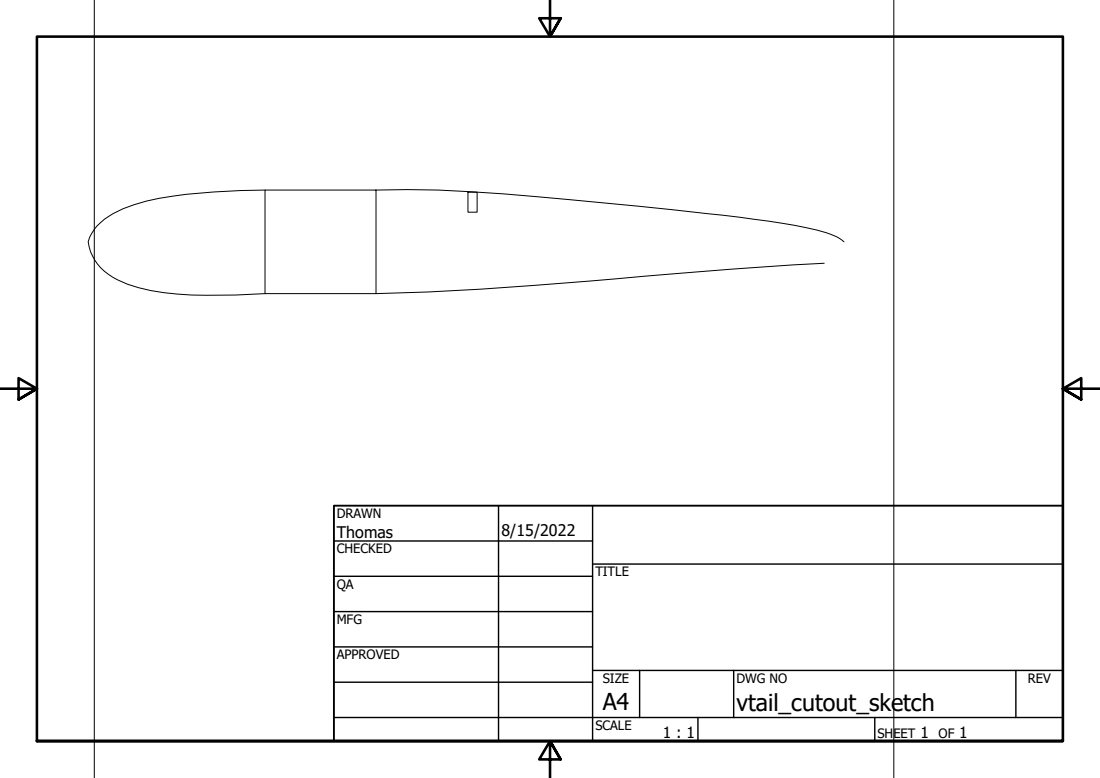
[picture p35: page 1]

DRAWN Thomas | 8/15/2022

CHECKED

TITLE

MFG

APPROVED

SIZE A4 | DWG NO vtail_cutout_sketch | REV

SCALE 1 : 1 | SHEET 1 OF 1

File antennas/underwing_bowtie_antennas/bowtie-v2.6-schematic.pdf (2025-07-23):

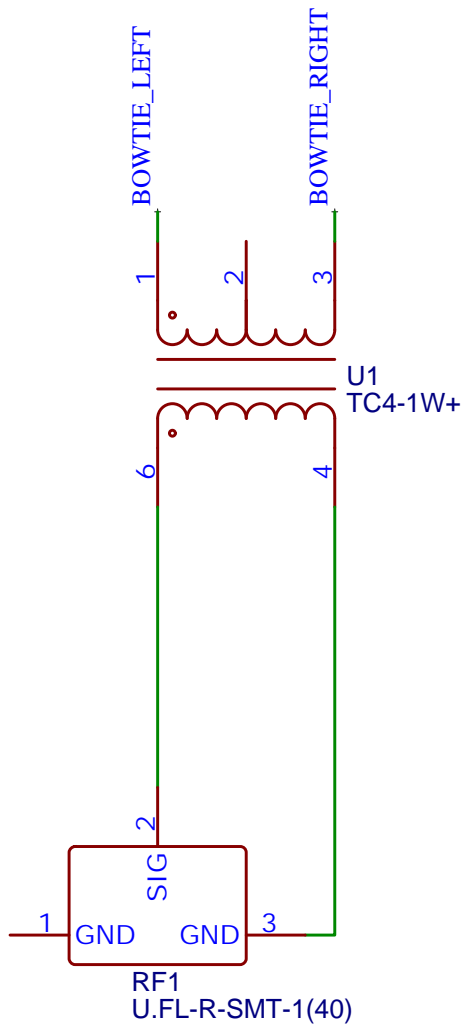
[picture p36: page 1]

Company: Stanford Radio Glaciology

Drawn By: Thomas Teisberg

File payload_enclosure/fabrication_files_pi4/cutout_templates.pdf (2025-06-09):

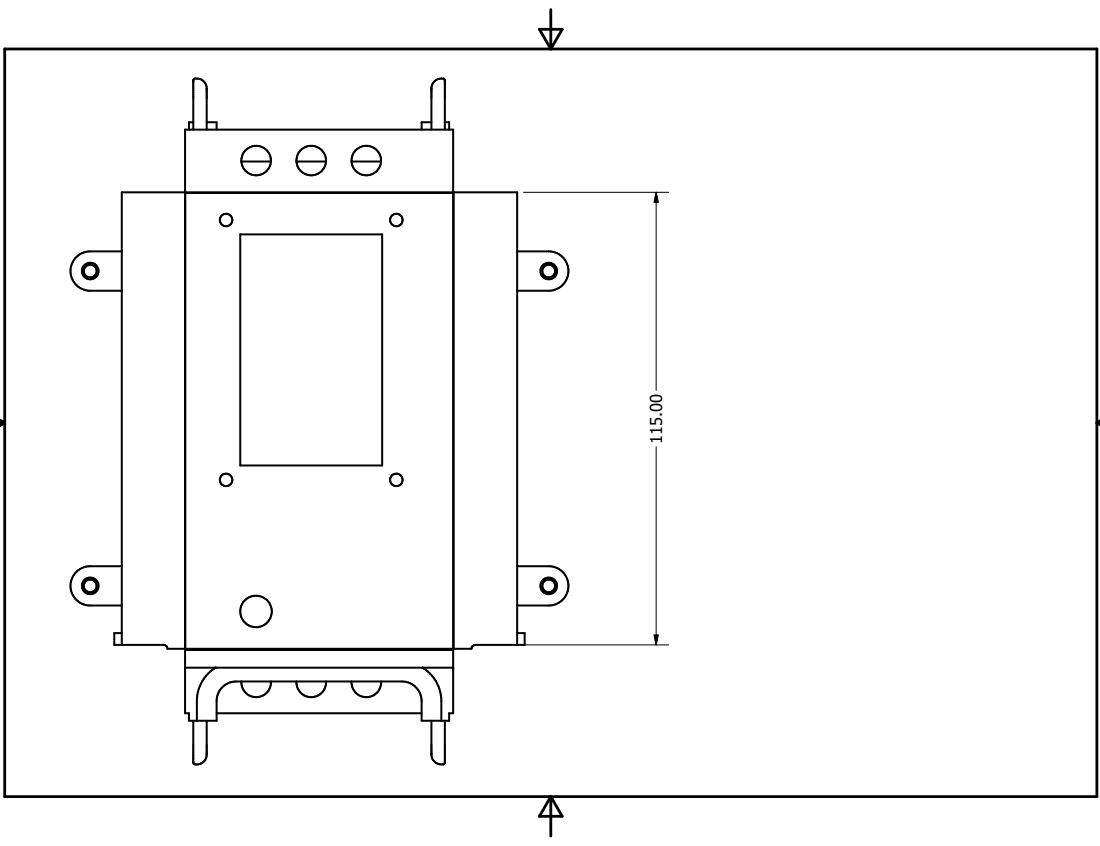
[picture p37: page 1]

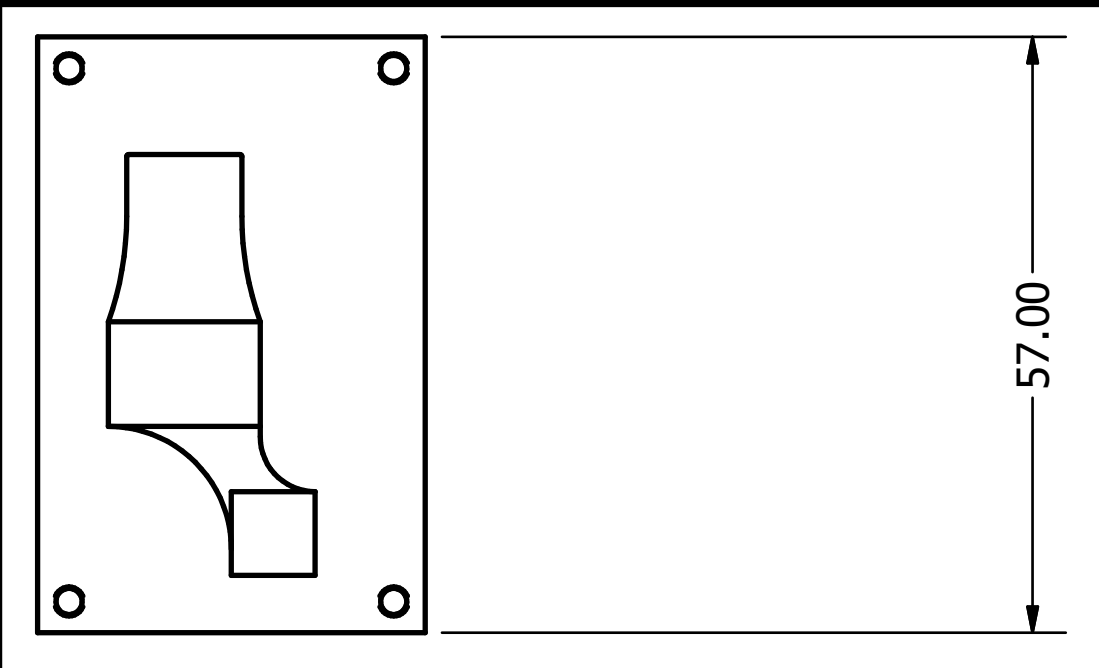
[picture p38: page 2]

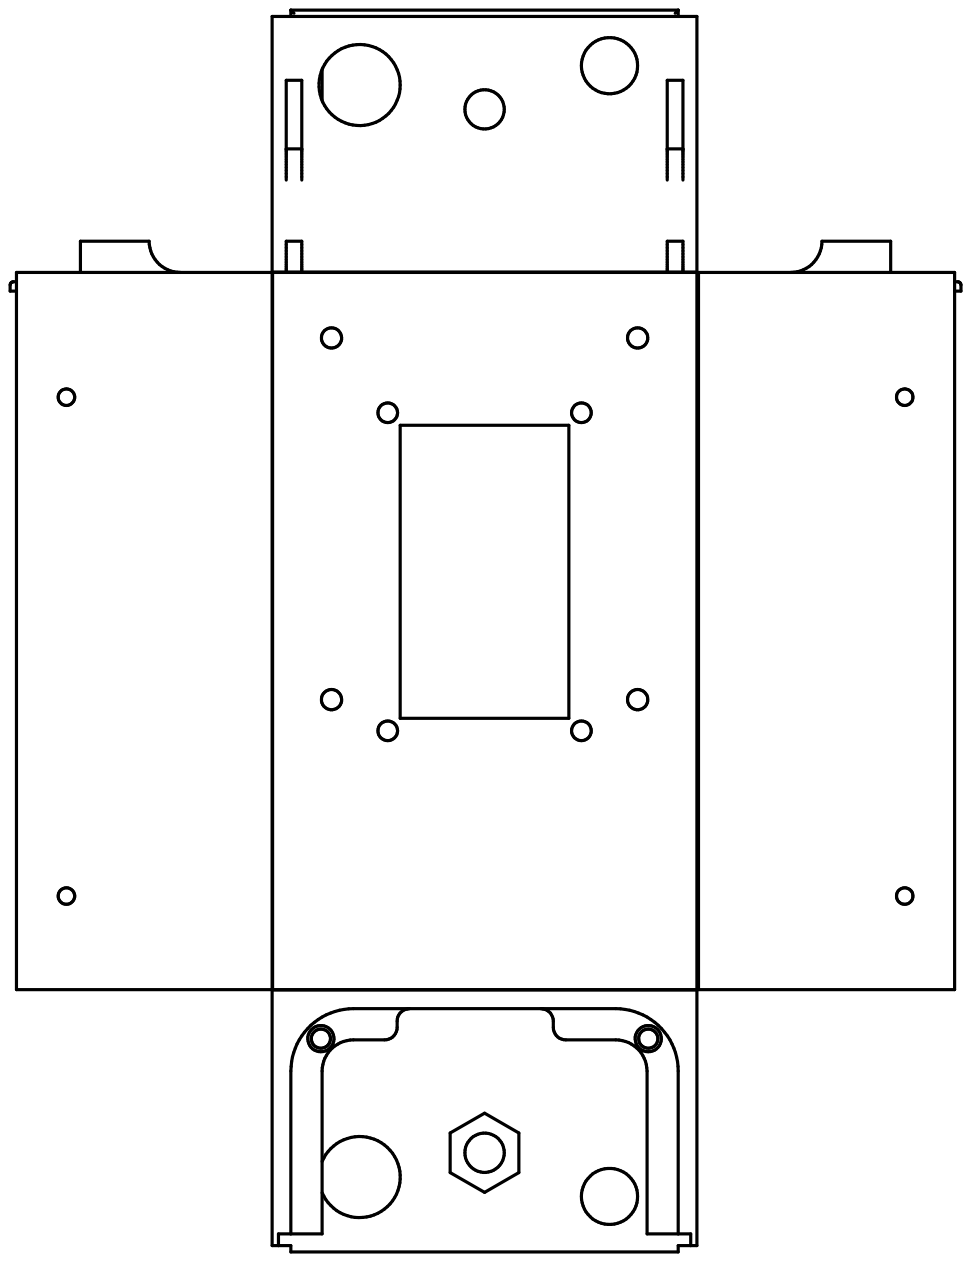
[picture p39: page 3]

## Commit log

2025-06-09 Initial commit of payload enclosure design files
    [cover_plate_2holes_standardfit_0p5mm_tol.dxf, fixture_pi_guide_pin.ipt, fixture_pi_guide_pin.stl, pi5_heat_block.stp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]
2025-06-09 Add payload enclosure images to readme
2025-07-23 Add enclosure PCBs
2025-07-23 Add fabrication files for payload pcbs
    [BOM_payload-divider-v4_2025-07-22.csv, BOM_uav-pi-hat-v4_2025-07-22.csv, PickAndPlace_PCB_Payload-Divider-v4_2025-07-22.csv, PickAndPlace_uav-pi-hat-v4-pcb_202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]
2025-07-23 Add 5v pcba
    [BOM_uav-5v-supply-v4_2025-07-22.csv, PickAndPlace_PCB_uav-5v-supply-v4_2025-07-22.csv]
2025-07-23 Add battery power distribution pcba
    [BOM_batt-power-distribution_2025-07-22.csv, PickAndPlace_PCB_batt-power-distribution_2025-07-22.csv]
2025-08-05 add peregrine 3D printed parts
    [1535 Bottom Tub.STEP, 1535 Top Tub.STEP, 1535_bottom_assembly.iam, 1535_top_assembly.iam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]
2025-09-14 Add 5V LNA power supply
    [BOM_5v-lna-supply_2025-09-14.csv, PickAndPlace_PCB_5v-lna-supply_2025-09-14.csv]
